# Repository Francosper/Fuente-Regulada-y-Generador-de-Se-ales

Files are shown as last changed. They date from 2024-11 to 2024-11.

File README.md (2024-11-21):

# Fuente Regulada - Generador de señales

## Descripción
Este proyecto consiste en el diseño y desarrollo de una fuente de tensión regulable que incorpora un generador de señales, pensado como una herramienta útil en laboratorios para proyectos de experimentación o entornos educativos. La fuente de alimentación está diseñada para ofrecer salidas de voltaje positivo y negativo, junto con una salida de tensión regulable según las necesidades que se requiera en una aplicación especifica. Además de su aplicación como fuente, el sistema incluye un generador de señales basado en el integrado XR2206CP el cual es un circuito integrado utilizado para la generación de distintos tipos de señales permitiendo generar señales senoidales, cuadradas y trignaulares. Su frecuencia de operación es configurable en un rango amplio que va desde 2 Hz hasta 1.3 MHz, lo que lo hace adecuado para una gran variedad de pruebas.
El generador de señales incorpora un mecanismo de ajuste tanto fino como grueso. Además, cuenta con un control de amplitud que permite al usuario variar la amplitud de las señales generadas según se quiera, la placa se presenta a continuación. 

<p align="center">
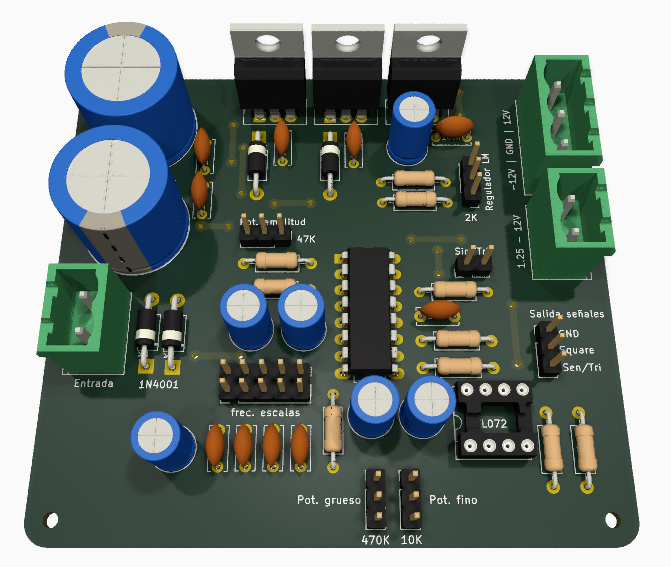
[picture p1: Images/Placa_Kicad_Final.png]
  
  <br>
  <em>Fig 1: Renderizado de la fuente regulada y generador de señales</em>
</p>

El artículo tiene como objetivo ofrecer una visión general de los componentes que componen el funcionamiento de la placa, abarcando sus principales características y especificaciones del sistema. Además, incluirá los archivos de software requeridos para su fabricacion, tales como los esquemas electrónicos, esquema de impresión de PCB, etc.

## Caracteristicas

A continuacion se nombran las caracteristicas de la placa 

| **Etapa**                     | **Descripción**                                           |
|------------------------------------|-----------------------------------------------------------|
| **Entrada de alimentación**        | Transformador de 20V eficaces                              |
| **Salidas de voltaje fijo**        | +12V y -12V                                               |
| **Salidas de voltaje regulable**   | 1.25V hasta 10V                                           |
| **Salidas de señales**             | Senoidal, cuadrada y triangular                           |
| **Variación de amplitud**          | Ajuste de amplitud de señales generadas (senoidales y triangulares) |
| **Variación de frecuencia**        | Ajuste fino y grueso de frecuencia con sus respectivas escalas |
| **Selector de señales**            | Switch para cambiar entre señal senoidal a triangular     |

- Escalas de frecuencia

Cada escala corresponde a las posiciones del selector de izquierda a derecha como se muestra a continuación
| **Escala** | **Rango**          |
|------------|--------------------|
| 1          | 2Hz – 220Hz        |
| 2          | 20Hz – 2.2KHz      |
| 3          | 450Hz – 50KHz      |
| 4          | 2KHz – 200KHz      |
| 5          | 25KHz – 1.3MHz     |

## Descripción general del hardware

Se detallan los componentes utilizados en el diseño, y se explica su funcionalidad dividida en módulos para facilitar la comprensión de cada parte del sistema.

- ### Fuente regulable +-12V

La implementación de la fuente consiste en un transformador reductor a 20 Volts eficaces. Mientras mayor sea la tensión eficaz de entrada peor es el rendimiento de la fuente, ya que esa tensión cae en los reguladores LM7812 y LM7912 aumentando la disipación de potencia teniendo la misma corriente de salida.

<p align="center">
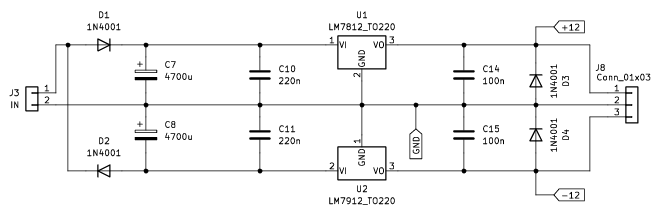
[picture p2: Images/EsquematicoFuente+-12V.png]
  
  <br>
  <em>Fig. 2: Esquemático de fuente regulada +-12V.</em>
</p>

- ### Fuente regulable 2V – 10V

El circuito de la fuente regulable mostrado a continuación utiliza directamente la salida de 12V generada por el circuito anterior (Fig. 2). Este diseño incluye un potenciómetro de 2 kΩ para permitir la variación de tensión, complementado con capacitores de filtro.

<p align="center">
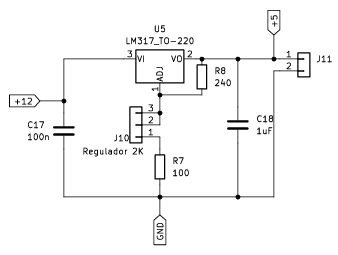
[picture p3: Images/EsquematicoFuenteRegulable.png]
  
  <br>
  <em>Fig.3: Esquemático de fuente regulable 2V – 10V.</em>
</p>

- ### Generador de señales

Debajo de la imagen se describe el funcionamiento de cada uno de los bloques para un mejor entendimiento.

<p align="center">
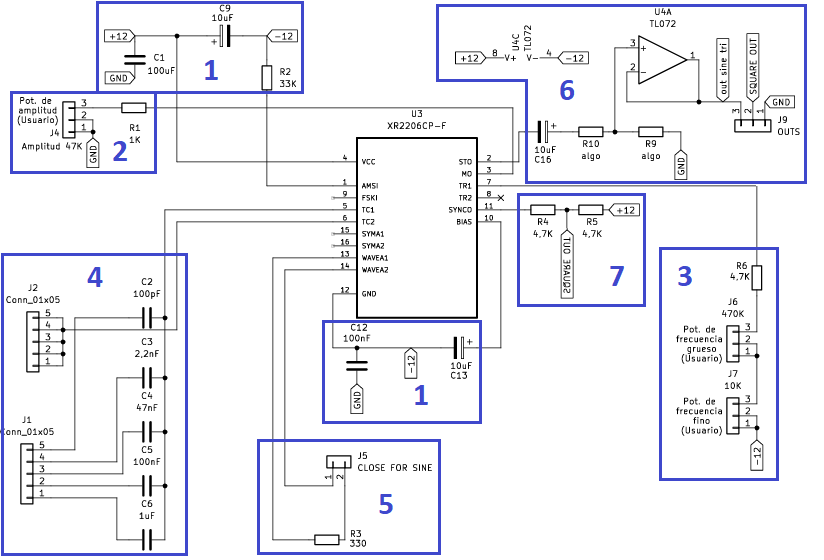
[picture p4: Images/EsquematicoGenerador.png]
  
  <br>
  <em>Fig.4: Esquemático del circuito generador de señales.</em>
</p>

| **Bloque** | **Descripción**                                                                                                                                   |
|------------|---------------------------------------------------------------------------------------------------------------------------------------------------|
| 1          | Alimentación: Toma los ±12V de la fuente regulable y cuenta con los filtros correspondientes para la reducción de ruido.                          |
| 2          | Control de amplitud: Afecta solamente la salida senoidal y triangular, permitiendo ajustar la amplitud de estas señales.                         |
| 3          | Control de frecuencia (parte resistiva): Modifica la resistencia del oscilador RC para variar la frecuencia de la señal de salida.                |
| 4          | Control de frecuencia (parte capacitiva): Modifica la capacidad del oscilador RC para variar la frecuencia de la señal de salida.                 |
| 5          | Selector de señales seno y triangular: Un switch que permite intercambiar entre señal senoidal y triangular en el pin de salida. Si el switch permanece cerrado se obtiene una señal senoidal, de otro modo, se tendrá una señal tipo triangular. |
| 6          | Salida de señales senoidal y triangular: Etapa de eliminación de continua, utilizando un operacional TL072 para aislar las señales y evitar la carga de la salida del XR2206. |
| 7          | Salida de señal cuadrada: Se toma desde un divisor resistivo y no tiene control de amplitud.                                                     |

## Fabricación del circuito

Se proporcionan los archivos necesarios para la fabricación de la placa, ya sea de manera casera, mediante el uso de una CNC, o para su envío a empresas de producción de circuitos profesionales. También se tendrá una tabla de los componentes necesarios.

Para descargar la carpeta con los archivos de KiCad visitar el siguiente link: [Carpeta de arcivos de KiCad](Archivos/Fuente)

A continuación, se muestran ambas caras de la placa.

<p align="center">
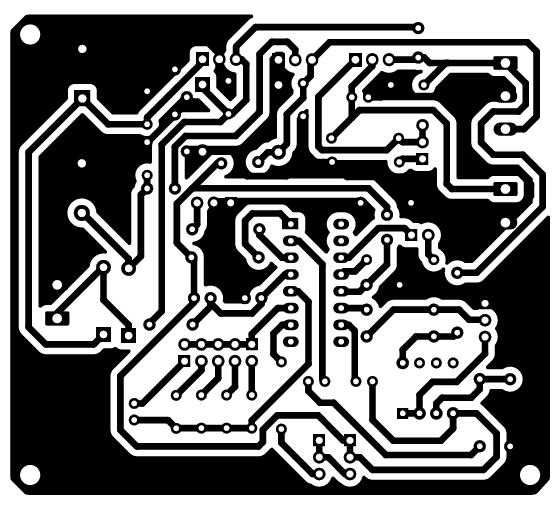
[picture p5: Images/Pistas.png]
  
  <br>
  <em>Fig.5: Pistas para fabricación del PCB.</em>
</p>

<p align="center">
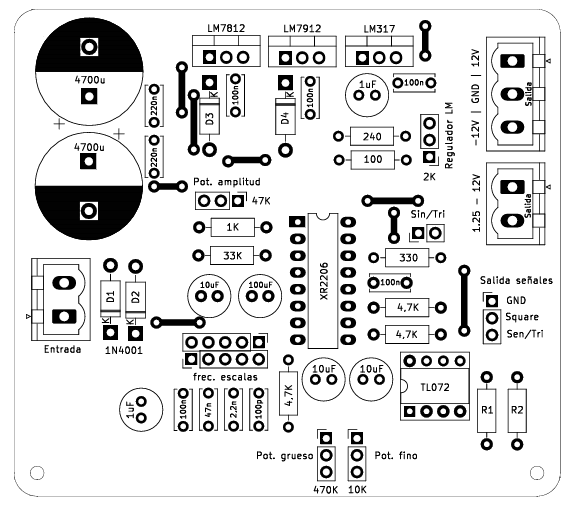
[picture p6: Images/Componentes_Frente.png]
  
  <br>
  <em>Fig.6: Disposición de los componentes del sistema.</em>
</p>

Si se desea descargar los esquematicos mostrados, se encuentran a continuacion:

- [Pistas (Capa inferior)](Archivos/Fuente%20Generadora%201.0%20Cobre.pdf)
- [Componentes (capa superior)](Archivos/Fuente%20Generadora%201.0%20Frente.pdf)

Los componentes necesarios para la fabricacion son se ven en la siguiente tabla.

### Componentes

| Componente               | Nota                          | Valor         |
|--------------------------|-------------------------------|---------------|
| **J3**                    | Conector Phoenix 2 Pines      | -             |
| **J11**                   | Conector Phoenix 2 Pines      | -             |
| **J8**                    | Conector Phoenix 3 Pines      | -             |
| **J9**                    | Conector 3 Pines              | -             |
| **J1**                    | Conector 5 Pines              | -             |
| **J2**                    | Conector (1 pin o 5 pines)    | -             |
| **J5**                    | Conector 2 Pines              | -             |
| **J4, J6**                | Conector 3 Pines p/potenciómetro | 500kΩ       |
| **J7**                    | Conector 3 Pines p/potenciómetro | 10kΩ        |
| **J10**                   | Conector 3 Pines p/potenciómetro | 2kΩ         |
| **C2**                    | Capacitor cerámico            | 100pF         |
| **C3**                    | Capacitor cerámico            | 2,2nF         |
| **C4**                    | Capacitor cerámico            | 47nF          |
| **C5, C12, C14, C15, C17** | Capacitor cerámico            | 100nF         |
| **C10, C11**              | Capacitor cerámico            | 220nF         |
| **C1**                    | Capacitor electrolítico       | 100uF         |
| **C6, C18**               | Capacitor electrolítico       | 1uF           |
| **C7, C8**                | Capacitor electrolítico       | 4700uF        |
| **C9, C13, C16**          | Capacitor electrolítico       | 10uF          |
| **D1, D2, D3, D4**        | Diodo                         | 1N4001        |
| **U1**                    | Regulador lineal 12V          | LM7812        |
| **U2**                    | Regulador lineal -12V         | LM7912        |
| **U5**                    | Regulador lineal              | LM317         |
| **U4A**                   | Amplificador Operacional      | TL072         |
| **R1**                    | Resistencia                   | 1kΩ           |
| **R2**                    | Resistencia                   | 33kΩ          |
| **R3**                    | Resistencia                   | 330Ω          |
| **R4, R5, R6**            | Resistencia                   | 4,7kΩ         |
| **R7**                    | Resistencia                   | 100Ω          |
| **R8**                    | Resistencia                   | 240Ω          |
| **R9**                    | Resistencia                   | 680Ω          |
| **R10**                   | Resistencia                   | 10kΩ          |

Si se busca tener un entendimiento mas profundo de sistema, tales como las curvas de regulacion, respuesta en frecuencia y otros tipos de comportamientos, se recomienda leer la hoja de datos que se presenta a continuacion: [Hoja de datos](Archivos/Hoja_de_datos_Fuente_Regulable_y_generador.pdf)

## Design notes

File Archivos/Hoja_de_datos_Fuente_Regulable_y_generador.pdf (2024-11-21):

ESTACIÓN DE TRABAJO | 1

## FUENTE REGULADA

## GENERADOR DE SEÑALES

- Fuente regulada +12V
- Fuente regulada -12V
- Fuente regulable 2V ~ 10V
- Generador de señales cuadrada – senoidal – triangular. 2 Hz ~ 1,3 MHz

## FUENTE REGULADA ±12V

La figura 1 muestra la implementación de la fuente. La entrada se toma de la red mediante un transformador reductor a 20 volts eficaces aproximadamente. Cuanto mayor es la tensión eficaz de entrada, peor es el rendimiento de la fuente puesto que esa tensión cae en los CI LM7812 y LM7912 aumentado la disipación de potencia para una misma corriente de salida.

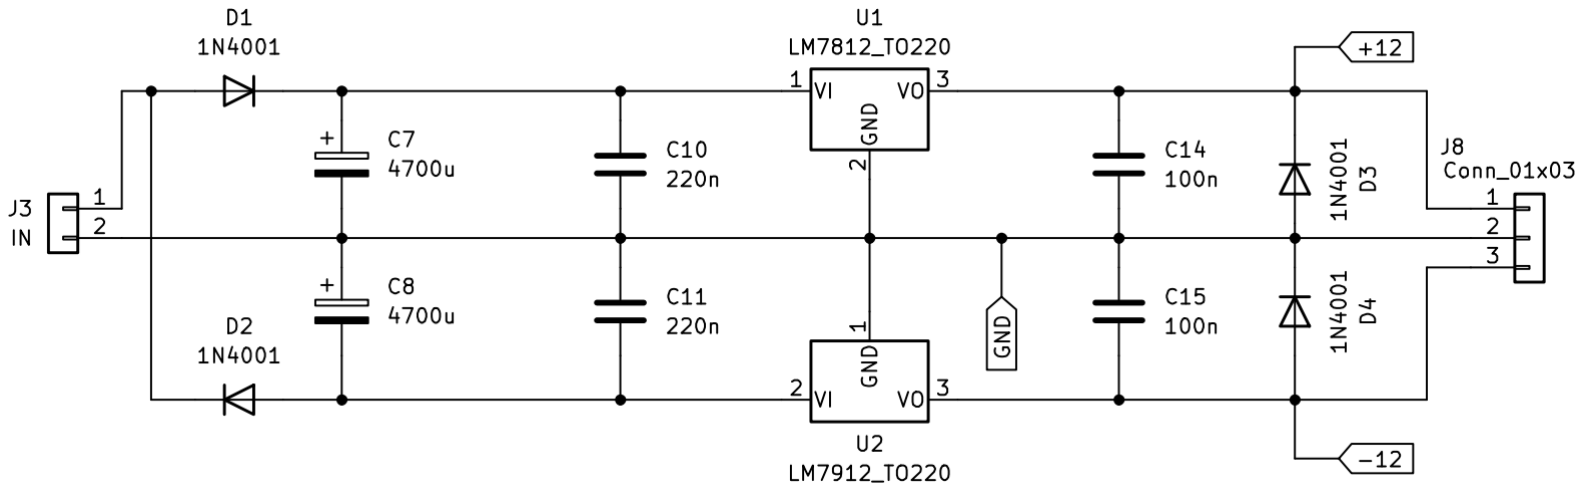
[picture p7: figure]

Figura 1. Esquemático del circuito de fuente regulada ±12V.

## FUENTE REGULABLE 2V ~ 10V

En la figura 2 se observa el circuito implementado para la fuente regulable. La alimentación del circuito se toma directamente de la salida de la fuente regulada +12V del circuito anterior.

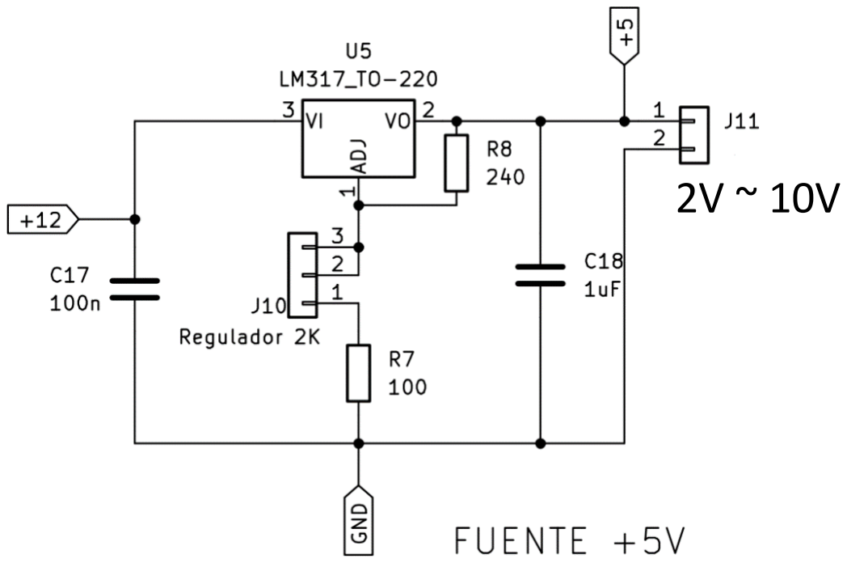
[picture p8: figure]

Figura 2. Esquemático del circuito de fuente regulable 2V ~ 10V.

2

## GENERADOR DE SEÑALES cuadrada – senoidal/triangular. 2 Hz ~ 1,3 MHz

El circuito del generador se implementó con el CI XR2206, como se aprecia en la figura 3.

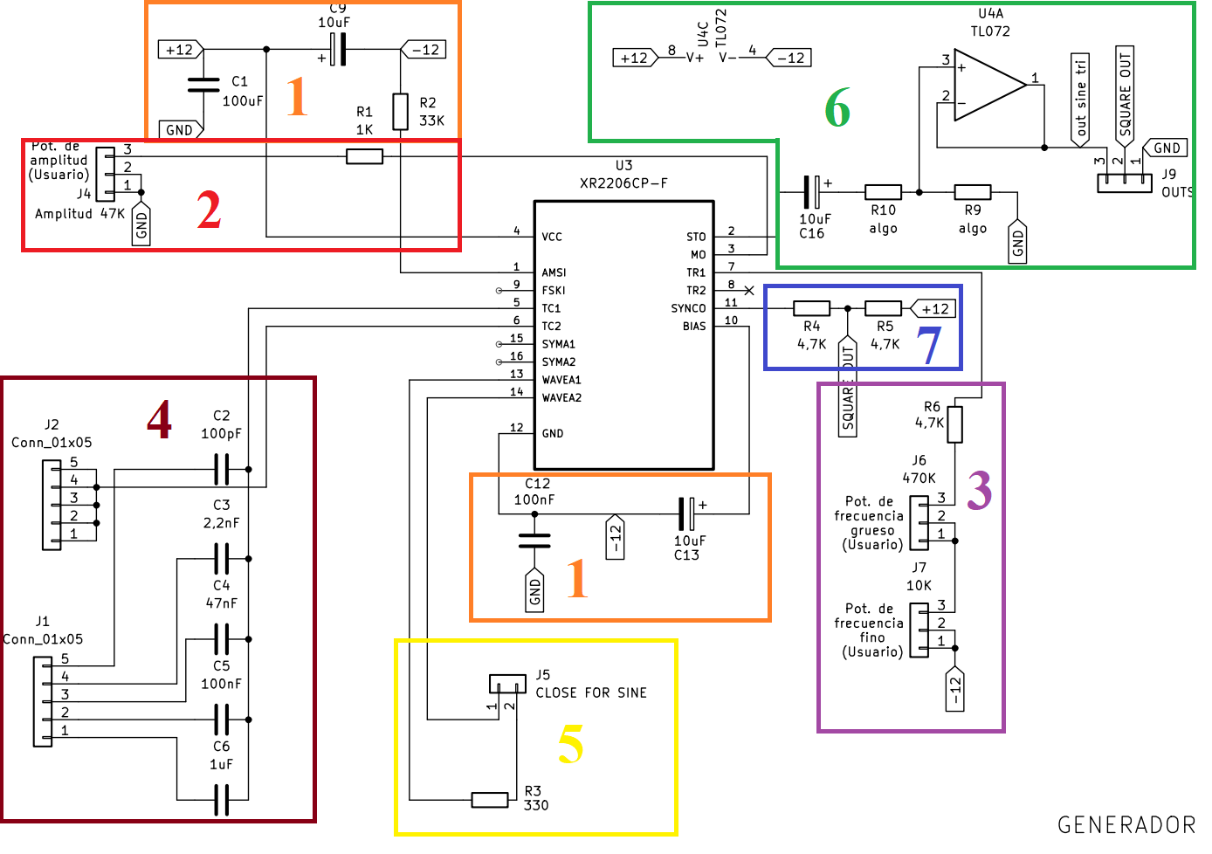
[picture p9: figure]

Figura 3. Esquemático del circuito generador de señales con XR2206.

A continuación se detalla el funcionamiento de cada bloque.

1. Alimentación ±12V y filtros.
2. Control de amplitud. Sólo la salida senoidal/triangular se ven afectadas por este control. La amplitud de salida senoidal vale aproximadamente 60mV por kΩ conectado al pin 3. La amplitud de salida triangular aproximadamente 160mV por kΩ conectado al pin 3.
3. Control de frecuencia. Modifica la R del oscilador RC, que sigue la siguiente ecuación:

f0 =

1
RC

[Hz]

4. Selector de capacitor del oscilador para modificar el rango de frecuencia. Siguiendo la misma ecuación, se modifica la capacidad entre 5 valores distintos, otorgando 5 escalas distintas de variación. Con los valores elegidos para este diseño esas escalas se observan en la tabla 1.

Tabla 1. Escalas de frecuencia del generador de señales.

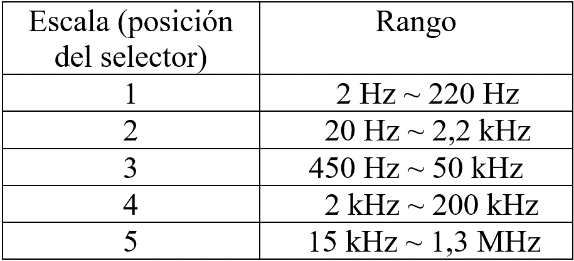
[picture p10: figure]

3

5. Los pines 13 y 14 deben estar conectados a través de una resistencia de 330ohm para tener una salida senoidal, o abiertos para tener una salida triangular. La resistencia debe ser lo más precisa posible pues la onda se deforma para otros valores de resistencia.
6. Salida senoidal/triangular. El capacitor se encarga de eliminar la componente de continua y se un amplificador operacional para no cargar la salida del XR2206. El divisor resistivo se utiliza para reducir la amplitud de la señal sin tener que reducir la amplitud de la salida del XR2206 a valores muy pequeños.
7. Salida de señal cuadrada. La salida se toma desde un divisor resistivo y no posee control de amplitud.

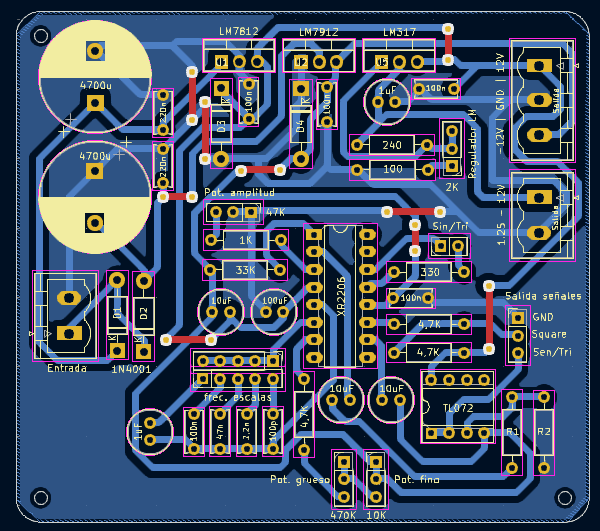
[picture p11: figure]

Figura 4. Diseño del circuito impreso completo.

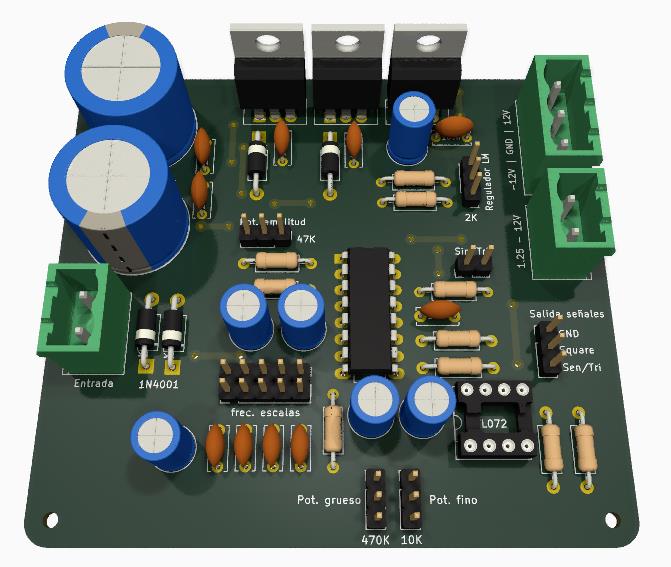
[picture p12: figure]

Figura 5. Renderizado 3D del circuito con los componentes montados.

4

Se realizaron curvas de regulación para evaluar el rendimiento del circuito. En las figuras TANTO se muestran las curvas de regulación de las fuentes sin disipador. La figura TANTO muestra la respuesta en frecuencia del generador de señales.

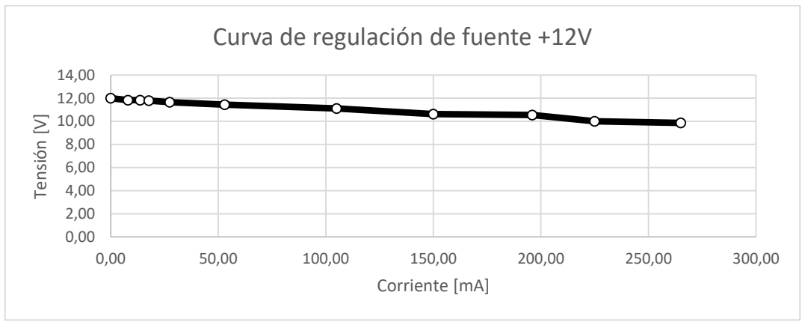
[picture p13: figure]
Tensión [V]; Corriente [mA]; Curva de regulación de fuente +12V

Figura 6. Curva de regulación de carga fuente +12V.

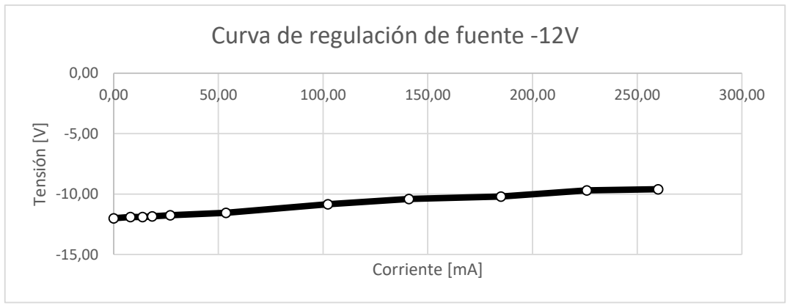
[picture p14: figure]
Tensión [V]; Corriente [mA]; Curva de regulación de fuente -12V

Figura 7. Curva de regulación de carga fuente -12V

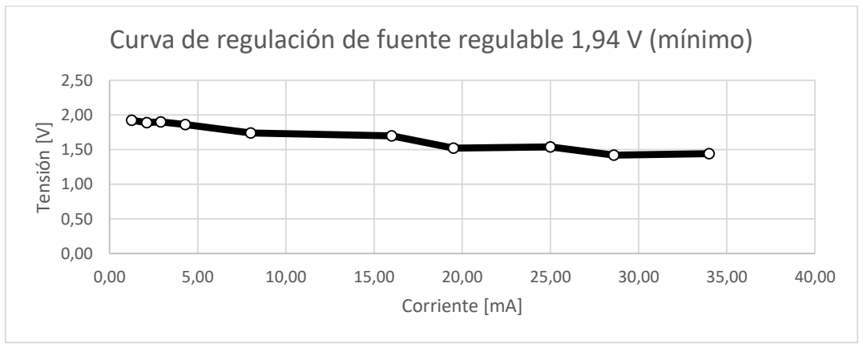
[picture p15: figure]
Tensión [V]; Corriente [mA]

Figura 8. Curva de regulación de carga fuente regulable al mínimo.

## Curva de regulación de fuente regulable 1,94 V (mínimo)

5

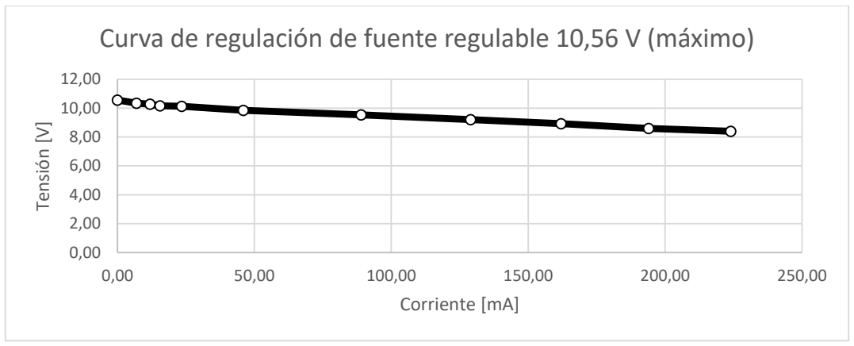
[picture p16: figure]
Tensión [V]; Corriente [mA]

Figura 9. Curva de regulación de carga fuente regulable al máximo.

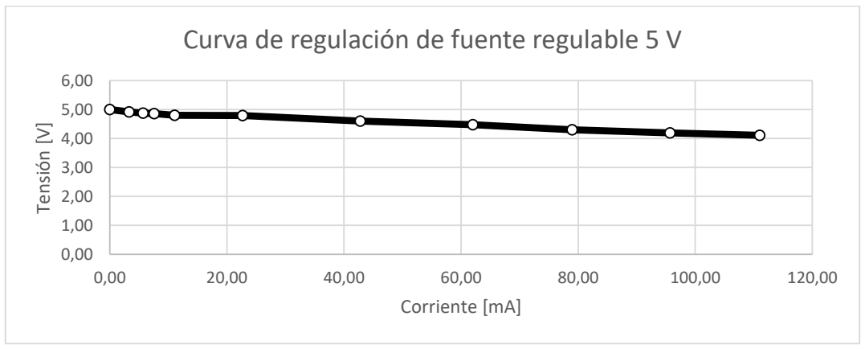
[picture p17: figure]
Tensión [V]; Corriente [mA]

Figura 10. Curva de regulación de carga fuente regulable ajustada a 5V en vacío.

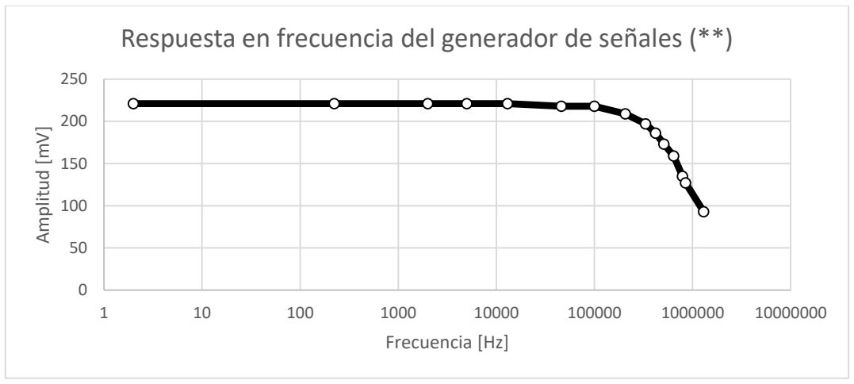
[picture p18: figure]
Amplitud [mV]; Frecuencia [Hz]

Figura 11. Respuesta en frecuencia del generador de señales para 220mV de amplitud.

## Curva de regulación de fuente regulable 10,56 V (máximo)

## Curva de regulación de fuente regulable 5 V

## Respuesta en frecuencia del generador de señales (**)

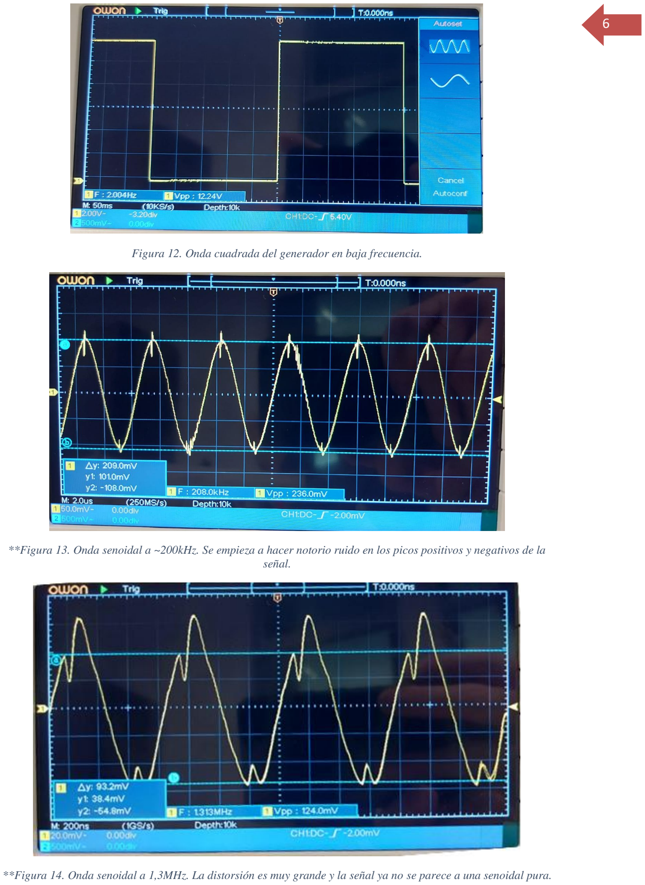
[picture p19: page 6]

6

Figura 12. Onda cuadrada del generador en baja frecuencia.

**Figura 13. Onda senoidal a ~200kHz. Se empieza a hacer notorio ruido en los picos positivos y negativos de la señal.

**Figura 14. Onda senoidal a 1,3MHz. La distorsión es muy grande y la señal ya no se parece a una senoidal pura.

7

La onda senoidal y triangular presenta que para amplitudes bajas se hace muy notorio. Este ruido de alta frecuencia puede atenuarse con filtros con una frecuencia de corte por encima de 1MHz. En las figuras 15 y 16 puede verse el efecto de agregar una red RC en serie con la salida. La señal se suaviza pero se empeora la respuesta en frecuencia debido a la respuesta de la red RC. Se pueden adoptar filtros con un corte más abrupto y respuesta más plana en la banda de paso.

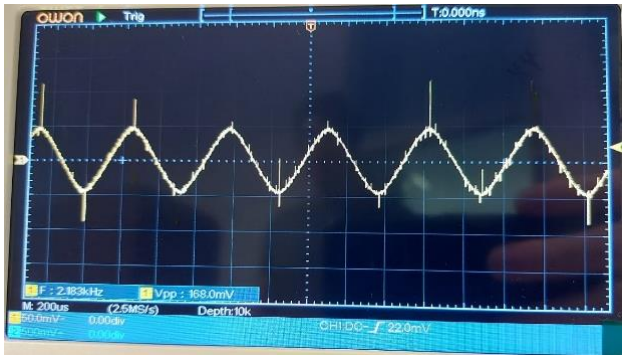
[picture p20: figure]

Figura 15. Presencia de ruido en la señal senoidal para amplitudes bajas.

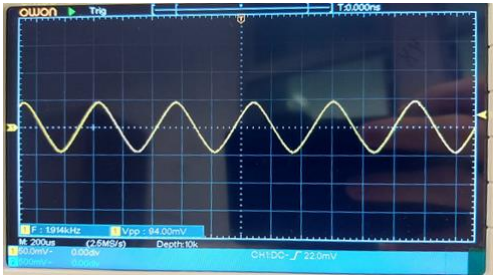
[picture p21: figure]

Figura 16. Eliminación del ruido con filtro RC con frecuencia de corte alta.

## LISTA DE COMPONENTES

Componente | Nota | Valor
J3 | Conector Phoenix 2 Pines | -
J11 | Conector Phoenix 2 Pines | -
J8 | Conector Phoenix 3 Pines | -
J9 | Conector 3 Pines | -
J1 | Conector 5 Pines | -
J2 | Conector (1 pin o 5 pines) | -

8

J5 | Conector 2 Pines | -
J4, J6 | Conector 3 Pines p/potenciómetro | 500kΩ
J7 | Conector 3 Pines p/potenciómetro | 10kΩ
J10 | Conector 3 Pines p/potenciómetro | 2kΩ
C2 | Capacitor cerámico | 100pF
C3 | Capacitor cerámico | 2,2nF
C4 | Capacitor cerámico | 47nF
C5, C12, C14, C15, C17 | Capacitor cerámico | 100nF
C10, C11 | Capacitor cerámico | 220nF
C1 | Capacitor electrolítico | 100uF
C6, C18 | Capacitor electrolítico | 1uF
C7, C8 | Capacitor electrolítico | 4700uF
C9, C13, C16 | Capacitor electrolítico | 10uF
D1, D2, D3, D4 | Diodo | 1N4001
U1 | Regulador lineal 12V | LM7812
U2 | Regulador lineal -12V | LM7912
U5 | Regulador lineal | LM317
U4A | Amplificador Operacional | TL072
R1 | Resistencia | 1kΩ
R2 | Resistencia | 33kΩ
R3 | Resistencia | 330Ω
R4, R5, R6 | Resistencia | 4,7kΩ
R7 | Resistencia | 100Ω
R8 | Resistencia | 240Ω
R9 | Resistencia | 680Ω
R10 | Resistencia | 10kΩ

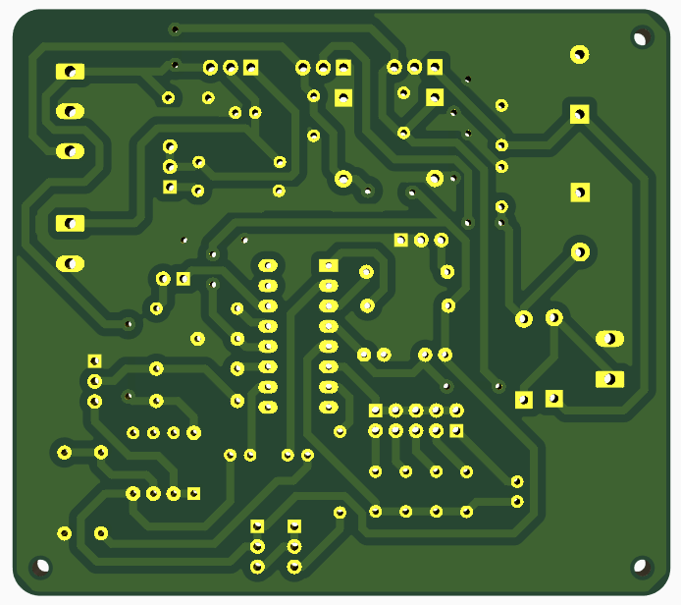
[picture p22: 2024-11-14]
Images/Placa_Kicad_Detras.png

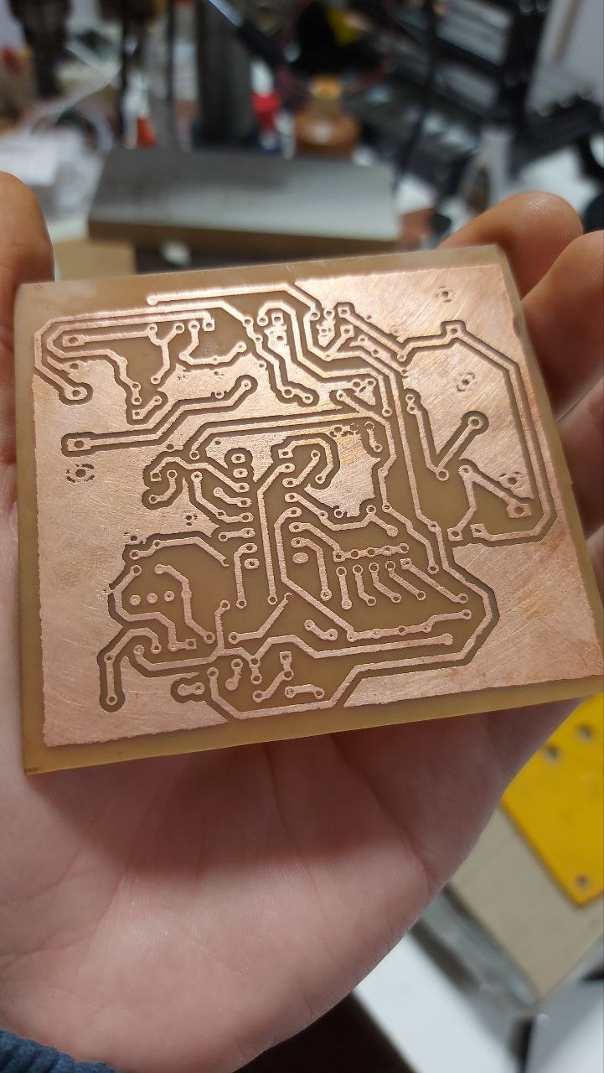
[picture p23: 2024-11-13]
Images/PlacaRevelada.jpg

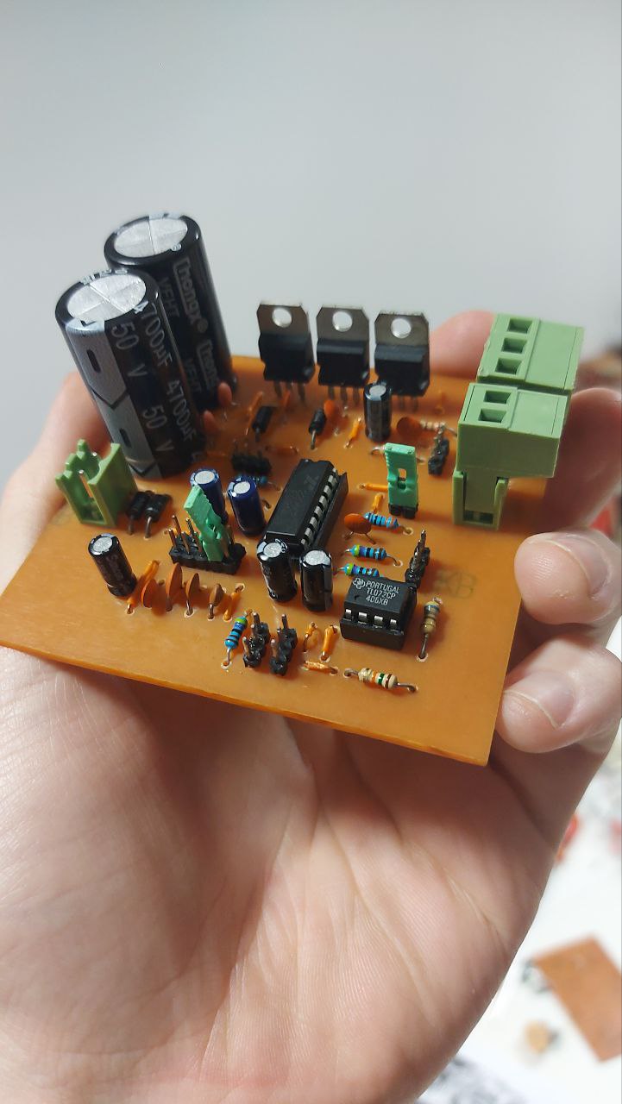
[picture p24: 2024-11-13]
Images/PlacaFinal.jpg

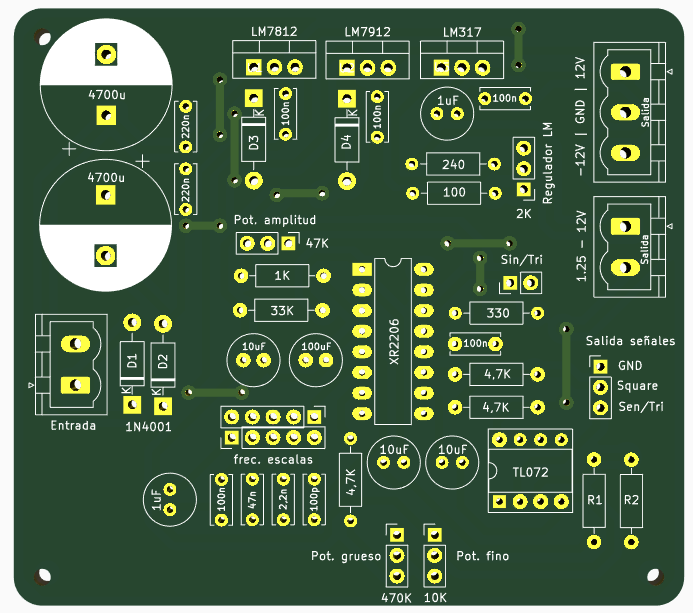
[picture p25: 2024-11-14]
Images/Placa_Kicad_Frente.png

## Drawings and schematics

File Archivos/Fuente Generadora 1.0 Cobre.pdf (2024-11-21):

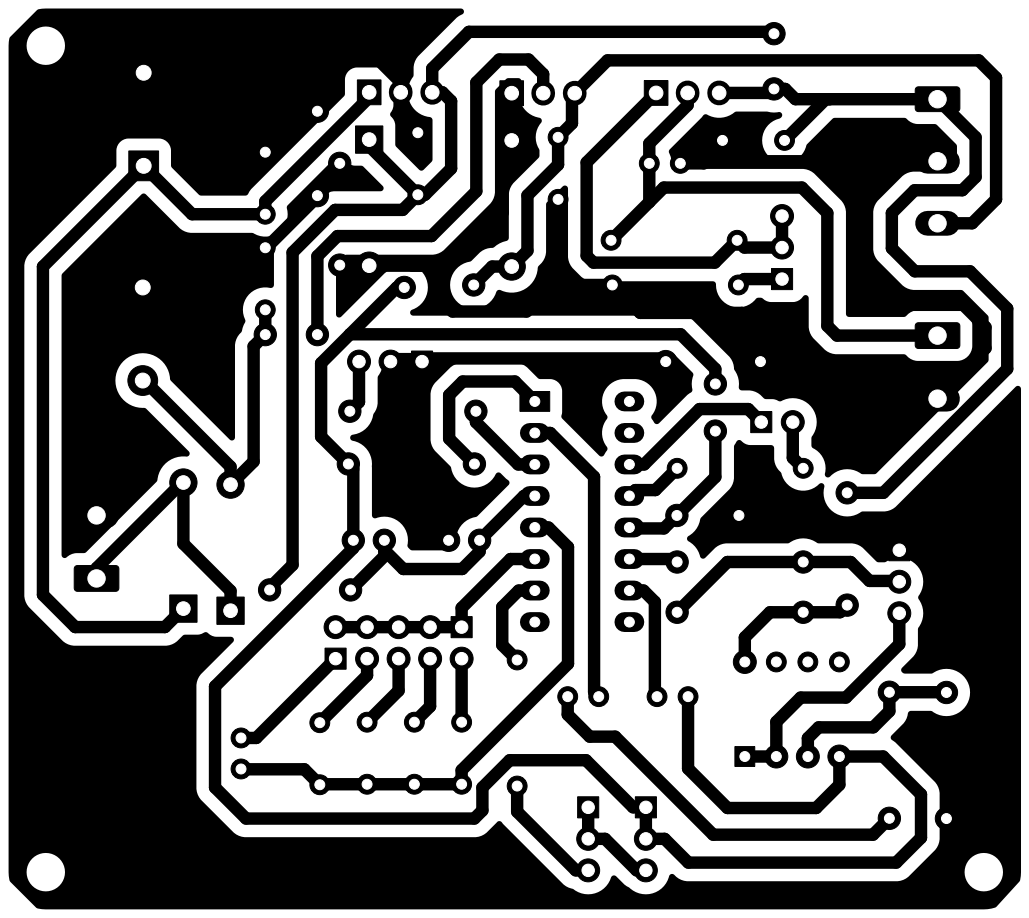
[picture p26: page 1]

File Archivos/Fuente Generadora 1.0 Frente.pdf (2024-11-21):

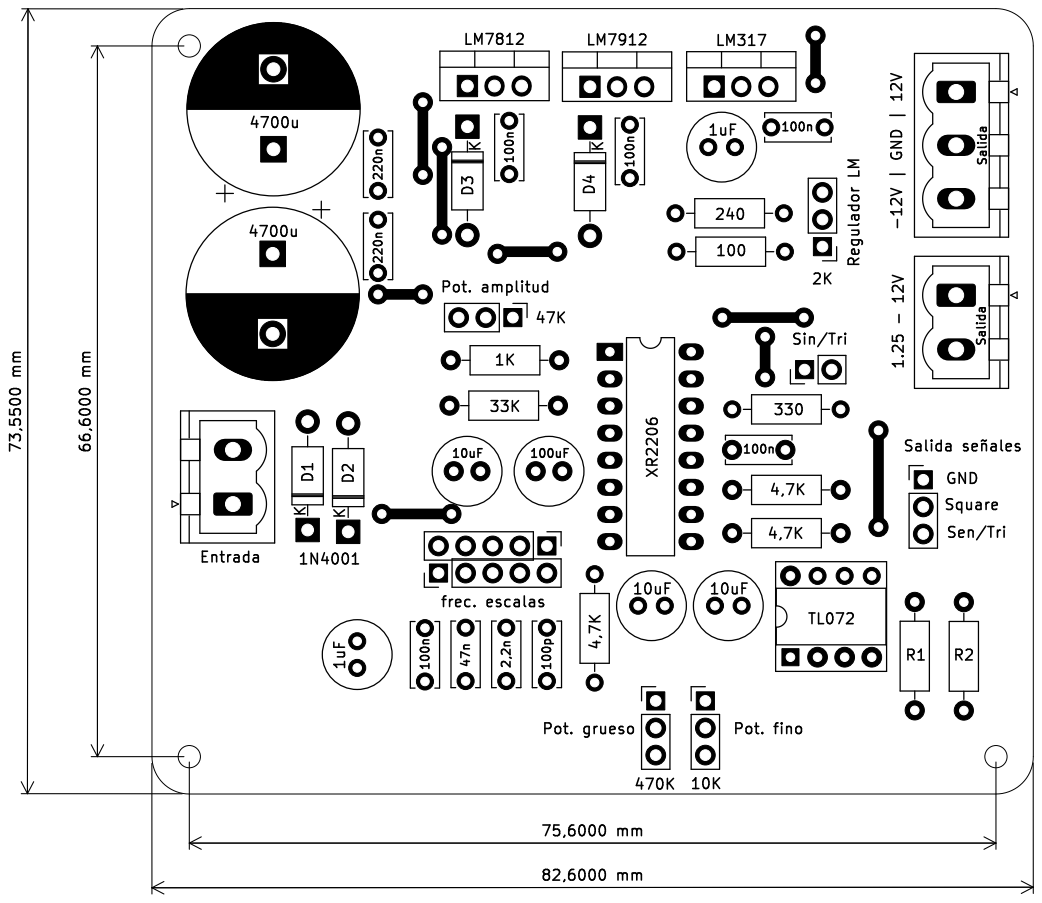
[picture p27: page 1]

Sen/Tri Square Pot. grueso

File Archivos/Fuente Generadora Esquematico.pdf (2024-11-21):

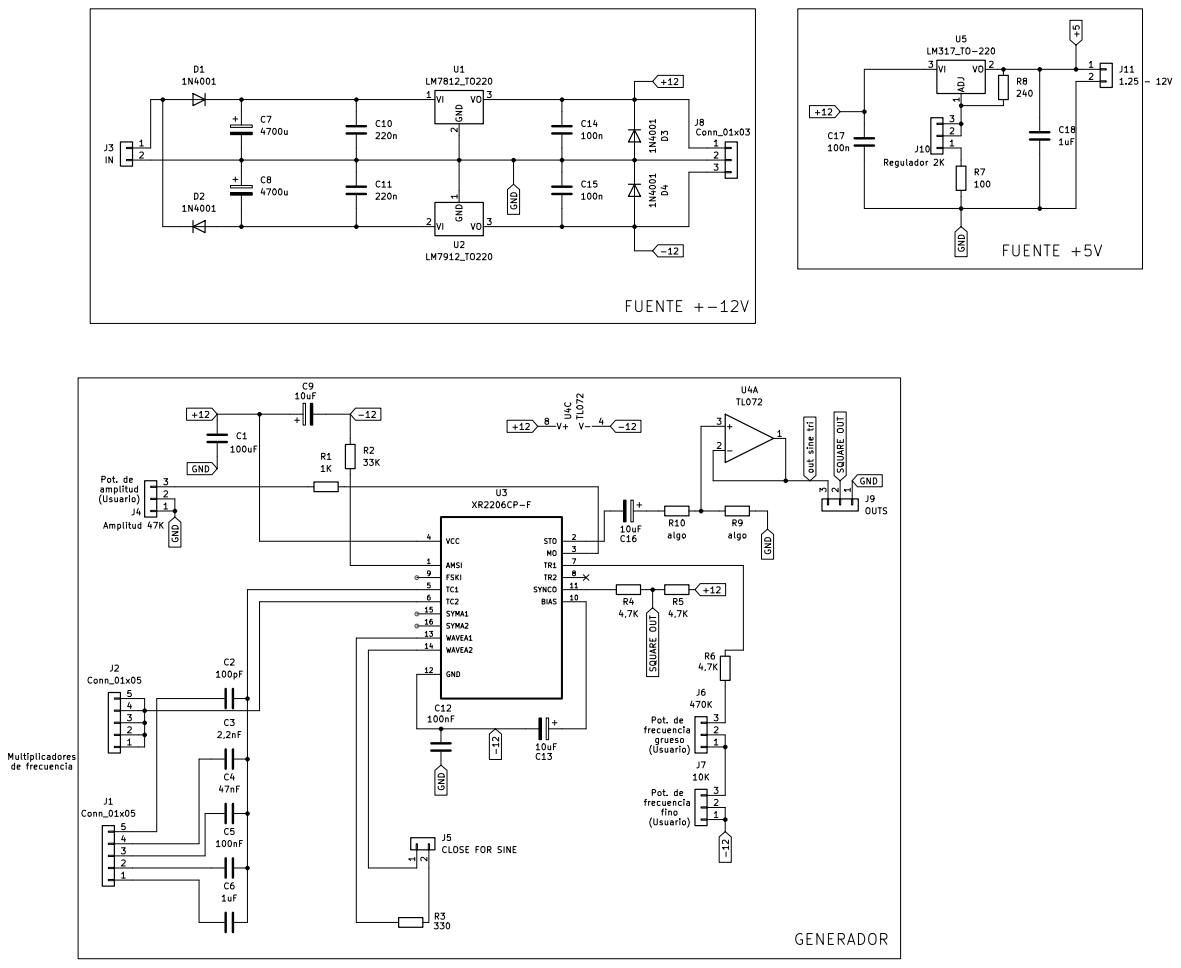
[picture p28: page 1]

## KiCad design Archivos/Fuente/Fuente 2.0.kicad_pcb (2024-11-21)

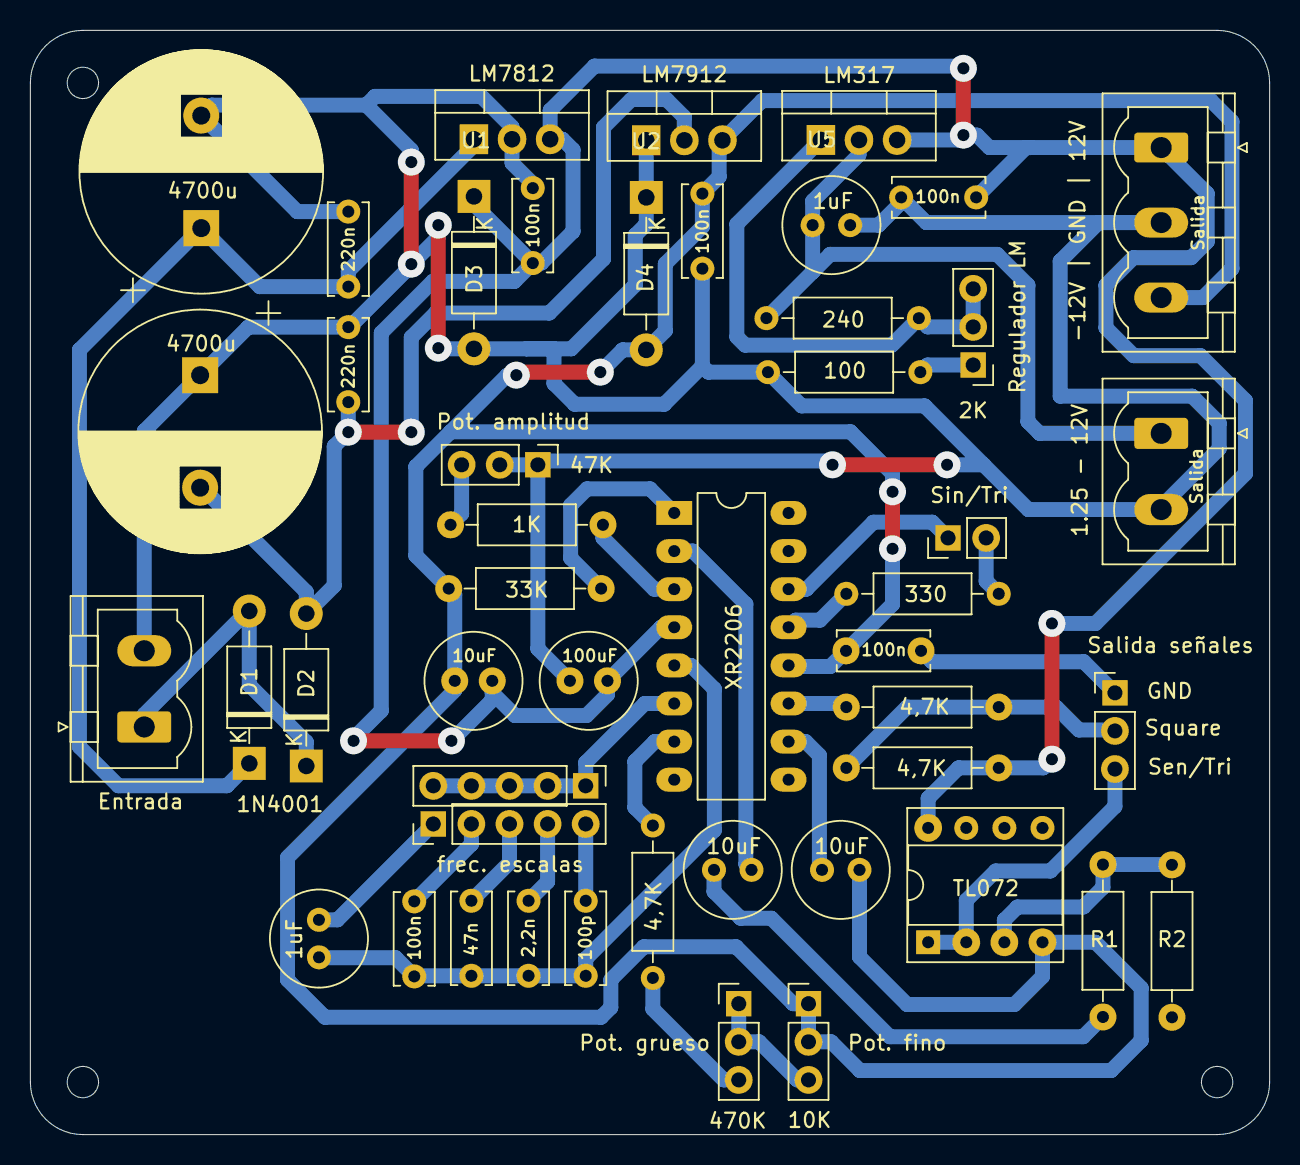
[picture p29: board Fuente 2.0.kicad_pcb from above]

Board: 2 copper layers, 82.6 x 73.6 mm, 48 parts (0 on the bottom side), 32 nets.

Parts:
C1: 100uF; C_Radial_D6.3mm_H11.0mm_P2.50mm
C2: 100p; C_Disc_D6.0mm_W2.5mm_P5.00mm
C3: 2,2n; C_Disc_D6.0mm_W2.5mm_P5.00mm
C4: 47n; C_Disc_D6.0mm_W2.5mm_P5.00mm
C5, C12, C14, C15, C17: 100n; C_Disc_D6.0mm_W2.5mm_P5.00mm
C6, C18: 1uF; C_Radial_D6.3mm_H11.0mm_P2.50mm
C7, C8: 4700u; CP_Radial_D16.0mm_P7.50mm
C9, C13, C16: 10uF; C_Radial_D6.3mm_H11.0mm_P2.50mm
C10, C11: 220n; C_Disc_D6.0mm_W2.5mm_P5.00mm
D1, D2, D3, D4: 1N4001; D_DO-41_SOD81_P10.16mm_Horizontal
J1, J2: Conn_01x05; PinHeader_1x05_P2.54mm_Vertical
J3: IN; PhoenixContact_MSTBVA_2,5_2-G-5,08_1x02_P5.08mm_Vertical
J4: Amplitud 47K; PinHeader_1x03_P2.54mm_Vertical
J5: Sin/Tri; PinHeader_1x02_P2.54mm_Vertical
J6: 470K; PinHeader_1x03_P2.54mm_Vertical
J7: 10K; PinHeader_1x03_P2.54mm_Vertical
J8: Conn_01x03; PhoenixContact_MSTBVA_2,5_3-G_1x03_P5.00mm_Vertical
J9: OUTS; PinHeader_1x03_P2.54mm_Vertical
J10: Regulador 2K; PinHeader_1x03_P2.54mm_Vertical
J11: 1.25 - 12V; PhoenixContact_MSTBVA_2,5_2-G-5,08_1x02_P5.08mm_Vertical
R1: 1K; R_Axial_DIN0207_L6.3mm_D2.5mm_P10.16mm_Horizontal
R2: 33K; R_Axial_DIN0207_L6.3mm_D2.5mm_P10.16mm_Horizontal
R3: 330; R_Axial_DIN0207_L6.3mm_D2.5mm_P10.16mm_Horizontal
R4, R5, R6: 4,7K; R_Axial_DIN0207_L6.3mm_D2.5mm_P10.16mm_Horizontal
R7: 100; R_Axial_DIN0207_L6.3mm_D2.5mm_P10.16mm_Horizontal
R8: 240; R_Axial_DIN0207_L6.3mm_D2.5mm_P10.16mm_Horizontal
R9, R10: algo; R_Axial_DIN0207_L6.3mm_D2.5mm_P10.16mm_Horizontal
U1: LM7812; TO-220-3_Vertical
U2: LM7912; TO-220-3_Vertical
U3: XR2206; DIP-16_W7.62mm_LongPads
U4: TL072; DIP-8_W7.62mm_Socket
U5: LM317; TO-220-3_Vertical

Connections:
+5: C18.2, J11.1, R8.2, U5.2 (VO)
+12: C1.1, C9.1, C14.1, C17.1, D3.1 (K), J8.1, R5.2, U1.3 (VO), U3.4 (VCC), U4.8 (V+), U5.3 (VI)
-12: C9.2, C12.1, C13.2, C15.2, D4.2 (A), J7.1, J7.2, J8.3, R2.1, U2.3 (VO), U3.12 (GND), U4.4 (V-)
GND: C1.2, C7.2, C8.1, C10.2, C11.1, C12.2, C14.2, C15.1, C17.2, C18.1, D3.2 (A), D4.1 (K), J3.2, J4.1, J4.2, J8.2, J9.1, J11.2, R7.1, R9.2, U1.2 (GND), U2.1 (GND)
unnamed: C16.1, R10.1
unnamed: D1.2 (A), D2.1 (K), J3.1
unnamed: C7.1, C10.1, D1.1 (K), U1.1 (VI)
unnamed: C8.2, C11.2, D2.2 (A), U2.2 (VI)
unnamed: C6.1, J1.1
unnamed: C5.1, J1.2
unnamed: C4.1, J1.3
unnamed: C3.2, J1.4
unnamed: C2.1, J1.5
unnamed: J2.1, J2.2, J2.3, J2.4, J2.5, U3.6 (TC2)
unnamed: J4.3, R1.1
unnamed: J5.1, U3.14 (WAVEA2)
unnamed: J5.2, R3.1
unnamed: J6.1, J6.2, J7.3
unnamed: J6.3, R6.2
unnamed: J10.1, R7.2
unnamed: J10.2, J10.3, R8.1, U5.1 (ADJ)
unnamed: R2.2, U3.1 (AMSI)
unnamed: C13.1, U3.10 (BIAS)
unnamed: R1.2, U3.3 (MO)
unnamed: C16.2, U3.2 (STO)
unnamed: R4.1, U3.11 (SYNCO)
unnamed: C2.2, C3.1, C4.2, C5.2, C6.2, U3.5 (TC1)
unnamed: R6.1, U3.7 (TR1)
unnamed: R3.2, U3.13 (WAVEA1)
unnamed: R9.1, R10.2, U4.3 (+)
SQUARE OUT: J9.2, R4.2, R5.1
out sine tri: J9.3, U4.1, U4.2 (-)
